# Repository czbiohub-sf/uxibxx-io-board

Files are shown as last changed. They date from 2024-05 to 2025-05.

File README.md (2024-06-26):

# uxibxx-io-board
## Introduction
This repository contains the hardware design data, firmware and a Python driver implementation for the UXIB*xx* "family" of digital I/O board~~s~~. This project is intended to provide minimum-friction tools for interfacing Python code to electrical stuff (turning loads on and off, reading switches, etc) in laboratory automation projects.

Currently the device "family" consists of a single example, UXIB-DN12, designed to control a bank of 12 loads such as solenoid valves.

## Directory contents
- `driver/` contains the `uxibxx` Python package used to control UXIB*xx* devices
- `firmware/` contains the source code for the AVR firmware
- `pcb/` contains the KiCAD EDA project files for the UXIB-DN12 PCB

## Getting started
If starting with an already-made UXIB*xx* device, just install the included `uxibxx` package and review the associated API documentation. No extra system-level driver is required on Windows, MacOS or Linux.

See the `README.md` in each subdirectory for further information.

## Licenses
Software source code is licensed under the BSD 3-Clause License. Hardware design files are licensed under CERN-OHL-W.
See the `LICENSE` file in each subdirectory for a copy of the applicable license terms.

## Support
This project is maintained by Greg Courville of the Bioengineering Platform at Chan Zuckerberg Biohub San Francisco.

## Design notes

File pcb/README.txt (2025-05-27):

This directory has KiCAD 8 source files and other documentation for the UXIB-DN12 valve/relay controller board:

soldriver_sch.pdf            Printable UXIB-DN12 schematic
soldrive_assembly_front.pdf  UXIB-DN12 component placement drawing, front side
soldrive_assembly_back.pdf   UXIB-DN12 component placement drawing, rear side

soldriver.kicad_pro          UXIB-DN12 KiCAD 8 project file
soldriver.kicad_sch          UXIB-DN12 schematic
soldriver.kicad_pcb          UXIB-DN12 PCB layout
footprints.pretty/           Project footprint library
sym/                         Project symbol library

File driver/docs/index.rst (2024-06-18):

``uxibxx`` module
=========================

Driver class
------------
.. autoclass:: uxibxx.UxibxxIoBoard
   :members: __init__, list_connected_devices, open_first_device, from_serial_portname, get_direction, set_direction, get_input, get_output, set_output, board_model, board_id, terminal_nos, input_nos, output_nos
   :member-order: bysource

Enums
-----
.. autoclass:: uxibxx.UxibxxIoBoard.IoDirection
   :members:

Exceptions
----------
.. autoclass:: uxibxx.UxibxxIoBoard.UxibxxIoBoardError
.. autoclass:: uxibxx.UxibxxIoBoard.DeviceNotFound
   :show-inheritance: True
.. autoclass:: uxibxx.UxibxxIoBoard.IdMismatch
   :show-inheritance: True
.. autoclass:: uxibxx.UxibxxIoBoard.InvalidTerminalNo
   :show-inheritance: True
.. autoclass:: uxibxx.UxibxxIoBoard.Unsupported
   :show-inheritance: True
.. autoclass:: uxibxx.UxibxxIoBoard.RemoteError
   :show-inheritance: True
.. autoclass:: uxibxx.UxibxxIoBoard.ResponseTimeout
   :show-inheritance: True
.. autoclass:: uxibxx.UxibxxIoBoard.BadResponse
   :show-inheritance: True

Usage example
-------------
.. literalinclude:: usage_example.py
   :language: python

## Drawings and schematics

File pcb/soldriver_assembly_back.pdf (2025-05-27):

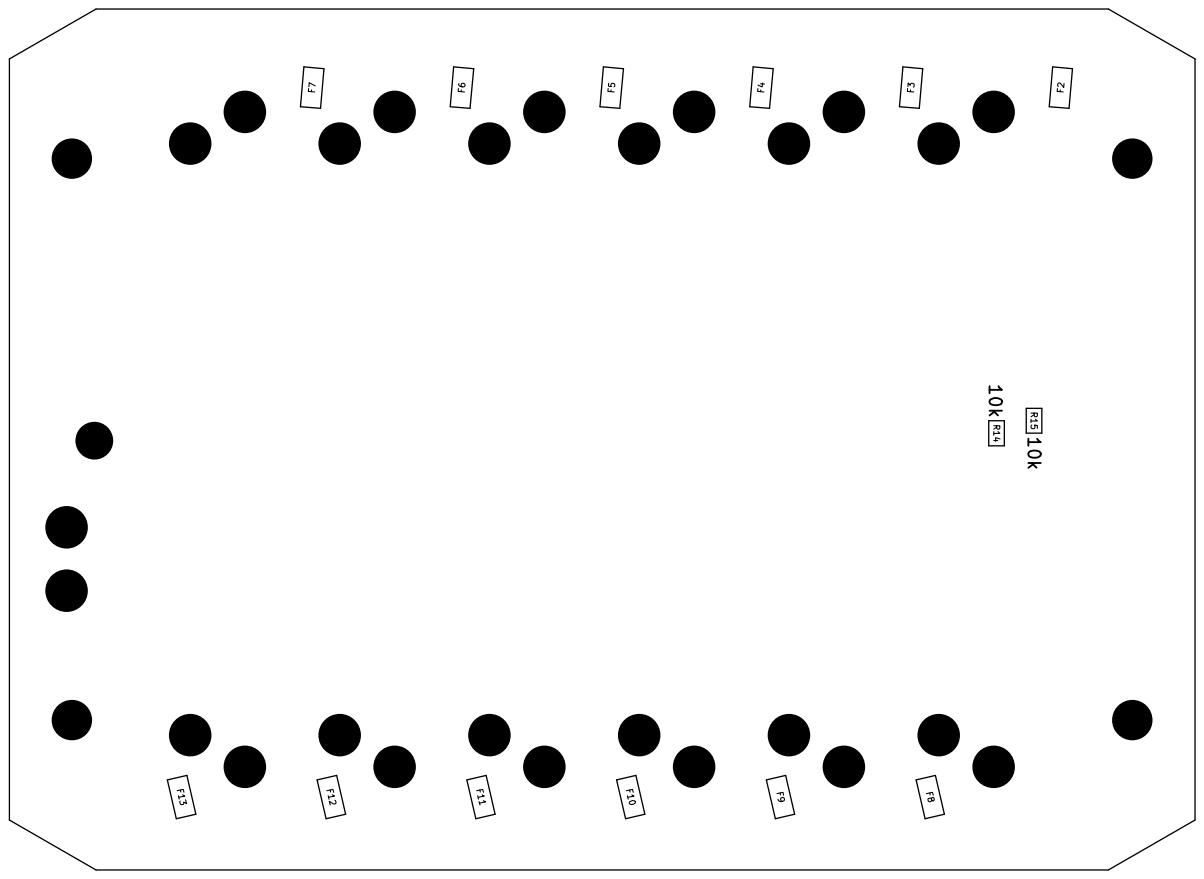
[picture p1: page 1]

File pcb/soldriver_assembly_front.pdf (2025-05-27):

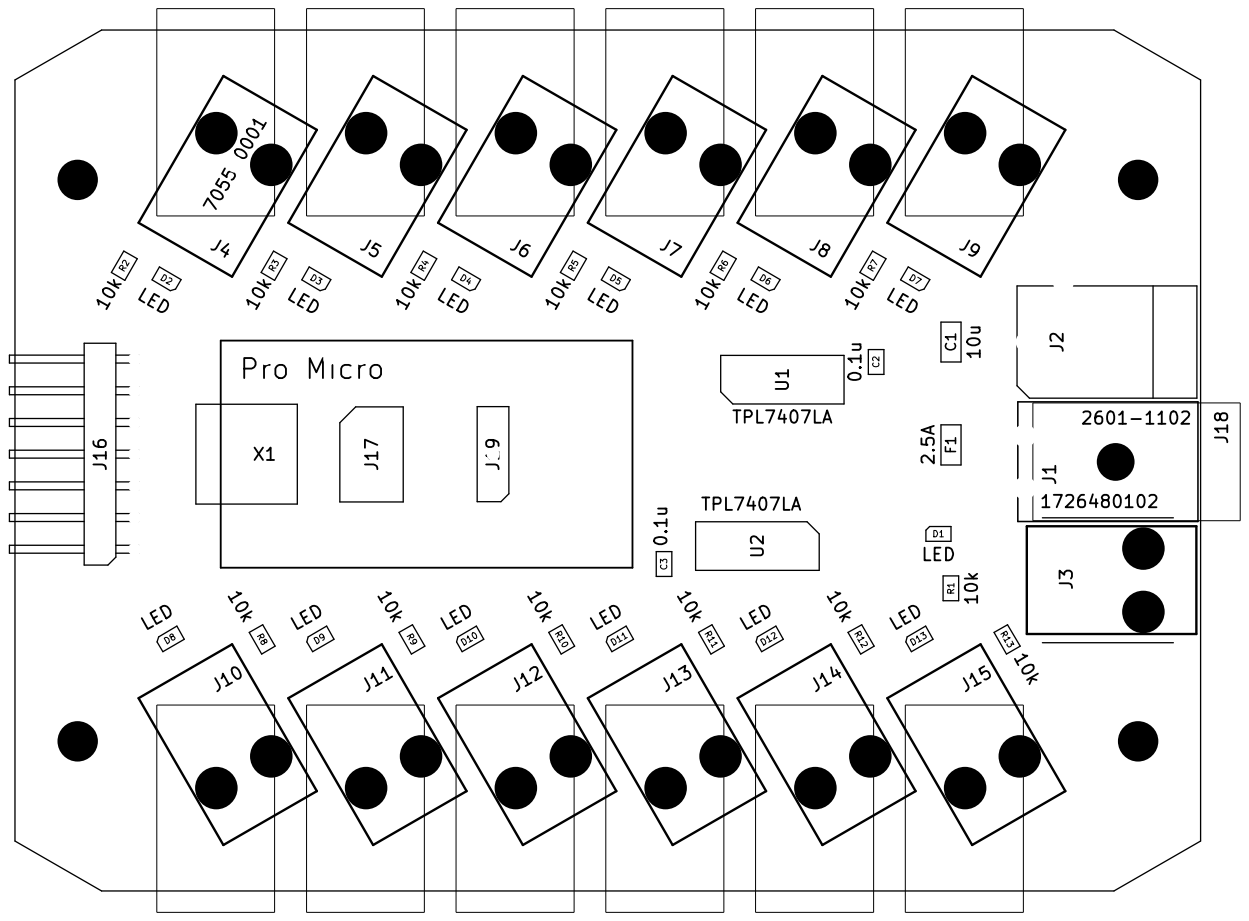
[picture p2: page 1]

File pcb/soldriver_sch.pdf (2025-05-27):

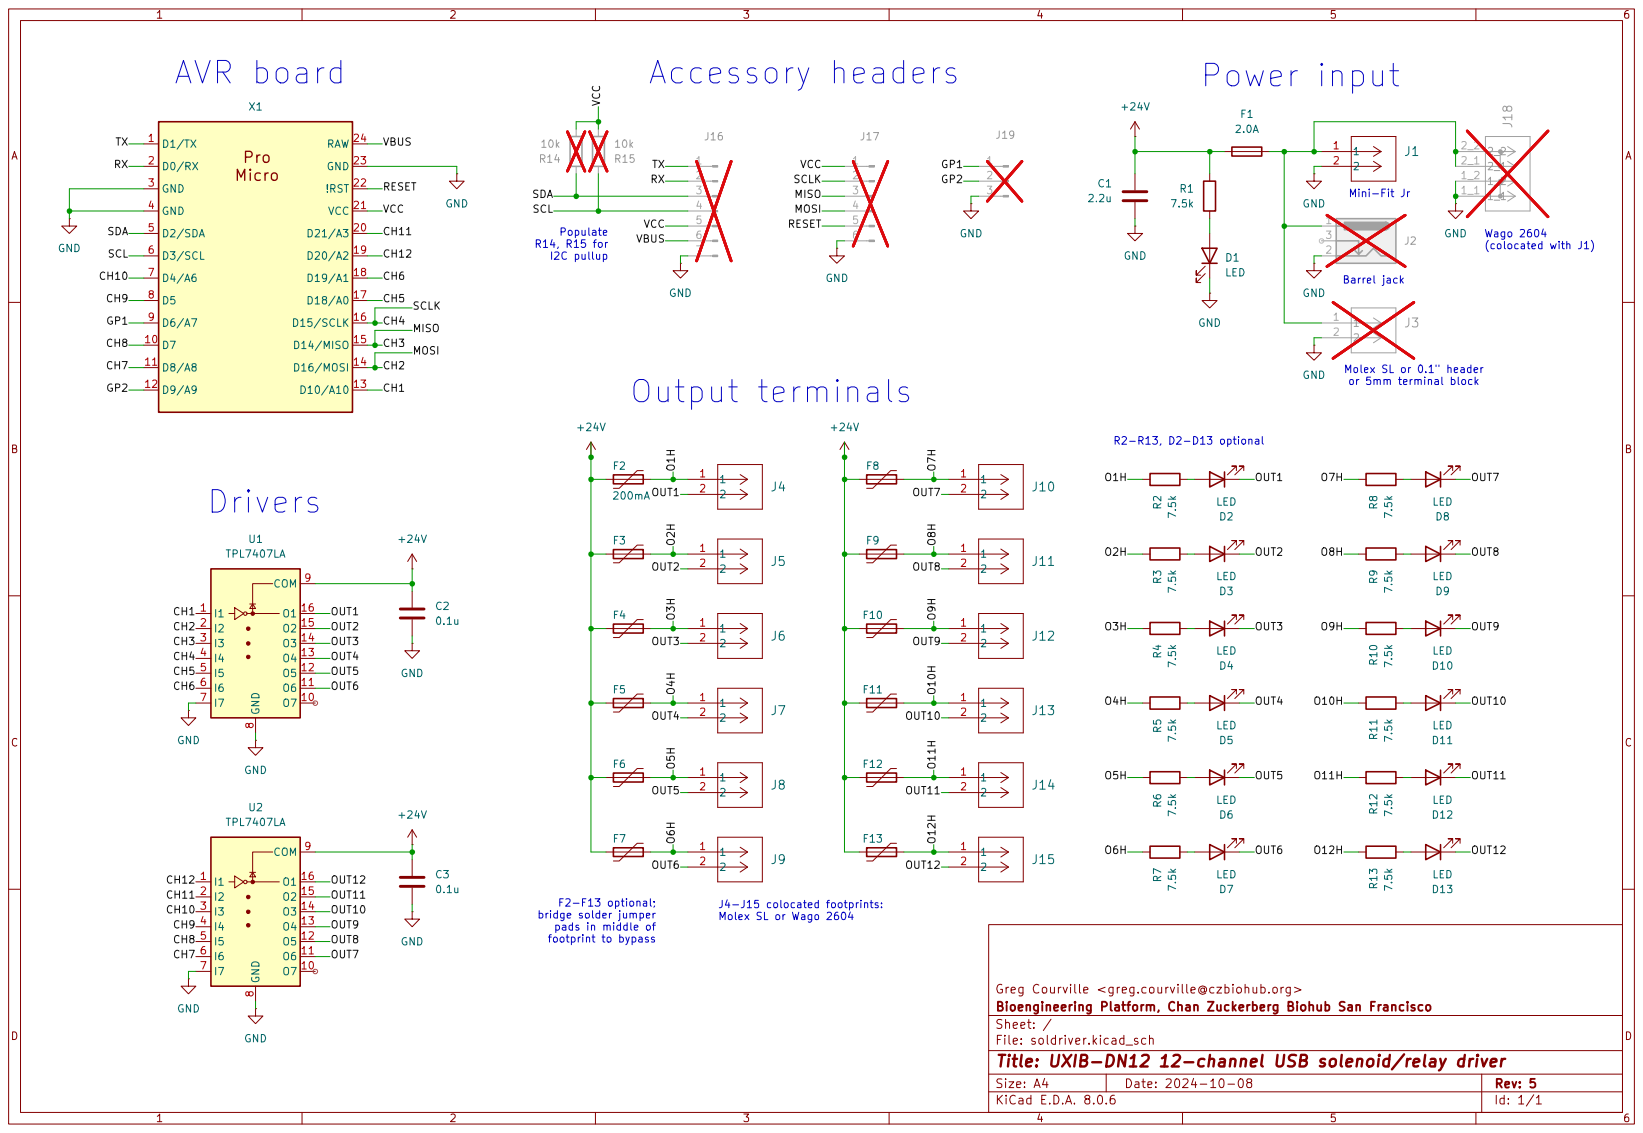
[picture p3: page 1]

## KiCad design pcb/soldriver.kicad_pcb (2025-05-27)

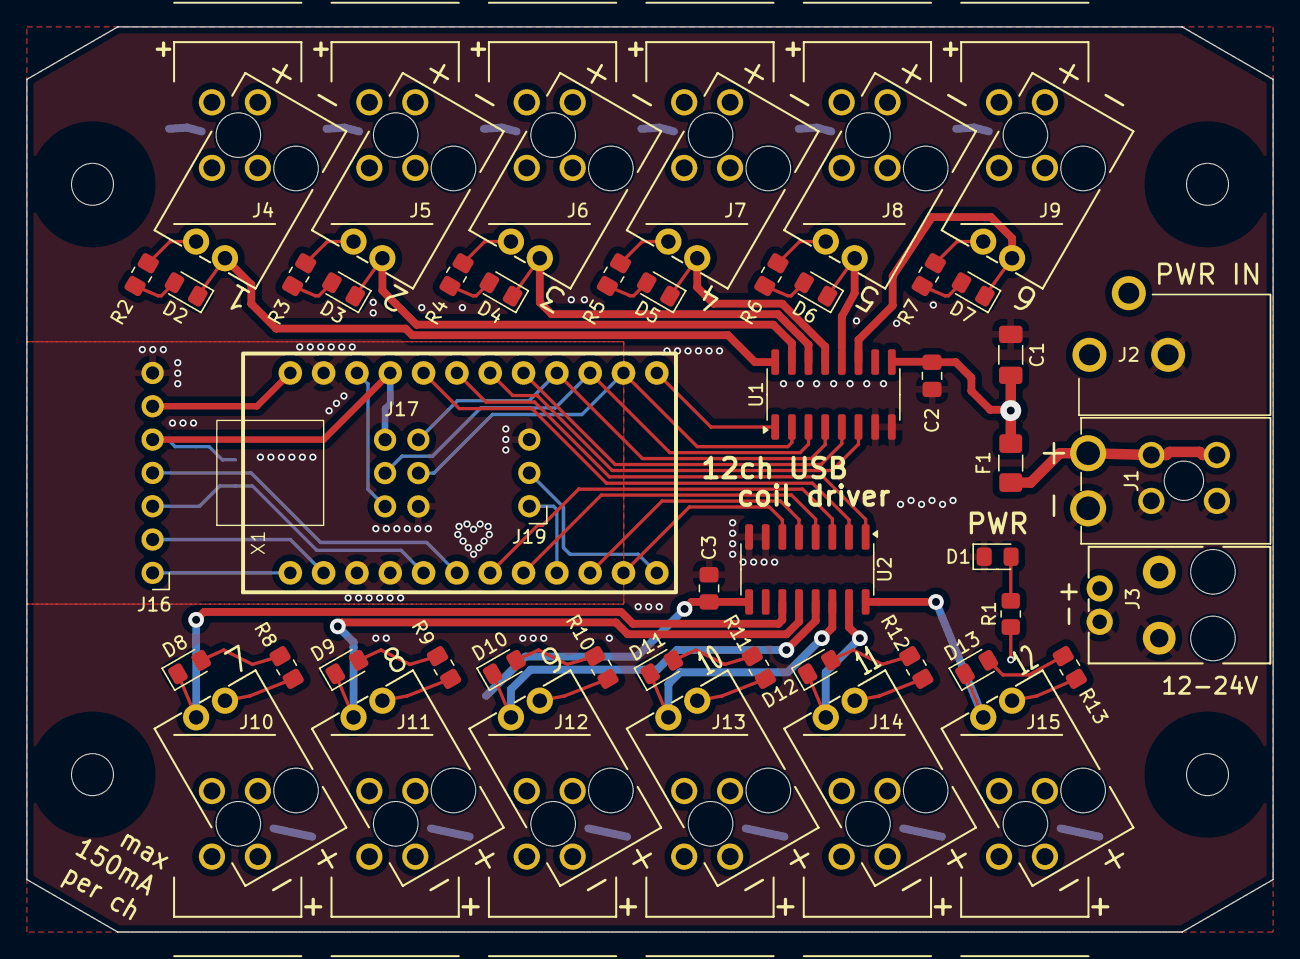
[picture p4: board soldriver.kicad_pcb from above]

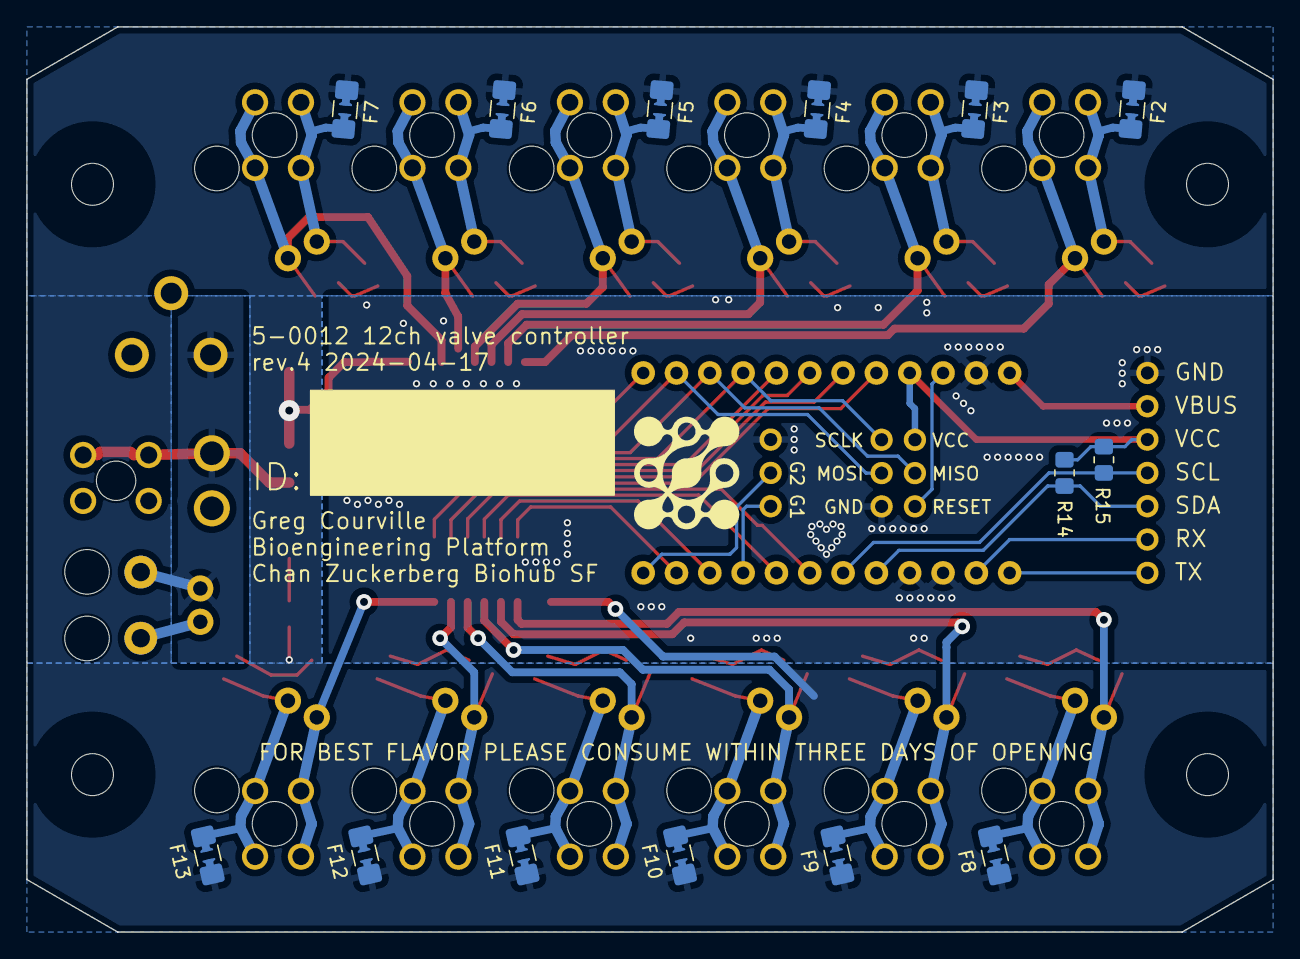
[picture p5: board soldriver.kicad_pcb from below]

Board: 2 copper layers, 95.0 x 69.0 mm, 70 parts (14 on the bottom side), 61 nets.

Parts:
C1: 10u; C_1206_3216Metric_Pad1.33x1.80mm_HandSolder
C2, C3: 0.1u; C_0805_2012Metric_Pad1.18x1.45mm_HandSolder
D1, D2, D3, D4, D5, D6, D7, D8, D9, D10, D11, D12, D13: LED; LED_0805_2012Metric_Pad1.15x1.40mm_HandSolder
F1: 2.5A; Fuse_1206_3216Metric_Pad1.42x1.75mm_HandSolder
F2, F3, F4, F5, F6, F7, F8, F9, F10, F11, F12, F13: Polyfuse; fuse_1206_jumperable
J1: 1726480102; CON_1726480102
J2: Barrel_Jack_Switch; CUI_PJ-102AH_with3dmodel
J3: 1726480102; molex_705510001_or_2pos_5mm_tb
J4, J5, J6, J7, J8, J9: 705510001; molex_705510001_or_wago_2601-1102_lh
J10, J11, J12, J13, J14, J15: 705510001; molex_705510001_or_wago_2601-1102_rh
J16: Conn_01x08_Pin; PinHeader_1x07_P2.54mm_Horizontal
J17: Conn_01x08_Pin; PinHeader_2x03_P2.54mm_Vertical
J18: 2601-1102; CONN_2601-1102_WAG
J19: Conn_01x03_Pin; PinHeader_1x03_P2.54mm_Vertical
MH1, MH2, MH3, MH4: MountingHole_3.2mm_M3
R1, R2, R3, R4, R5, R6, R7, R8, R9, R10, R11, R12, R13, R14, R15: 10k; R_0805_2012Metric_Pad1.20x1.40mm_HandSolder
U1, U2: TPL7407LA; SOIC-16_3.9x9.9mm_P1.27mm
X1: promicro_in_socket

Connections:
+24V: C1.1, C2.1, C3.1, F1.1, F2.1, F3.1, F4.1, F5.1, F6.1, F7.1, F8.1, F9.1, F10.1, F11.1, F12.1, F13.1, R1.1, U1.9 (COM), U2.9 (COM)
/CH1: U1.1 (I1), X1.13 (D10/A10)
/CH2: J17.4, U1.2 (I2), X1.14 (D16/MOSI)
/CH3: J17.3, U1.3 (I3), X1.15 (D14/MISO)
/CH4: J17.2, U1.4 (I4), X1.16 (D15/SCLK)
/CH5: U1.5 (I5), X1.17 (D18/A0)
/CH6: U1.6 (I6), X1.18 (D19/A1)
/CH7: U2.6 (I6), X1.11 (D8/A8)
/CH8: U2.5 (I5), X1.10 (D7)
/CH9: U2.4 (I4), X1.8 (D5)
/CH10: U2.3 (I3), X1.7 (D4/A6)
/CH11: U2.2 (I2), X1.20 (D21/A3)
/CH12: U2.1 (I1), X1.19 (D20/A2)
/GP1: J19.1, X1.9 (D6/A7)
/GP2: J19.2, X1.12 (D9/A9)
/O1H: F2.2, J4.1, R2.1
/O2H: F3.2, J5.1, R3.1
/O3H: F4.2, J6.1, R4.1
/O4H: F5.2, J7.1, R5.1
/O5H: F6.2, J8.1, R6.1
/O6H: F7.2, J9.1, R7.1
/O7H: F8.2, J10.1, R8.1
/O8H: F9.2, J11.1, R9.1
/O9H: F10.2, J12.1, R10.1
/O10H: F11.2, J13.1, R11.1
/O11H: F12.2, J14.1, R12.1
/O12H: F13.2, J15.1, R13.1
/OUT1: D2.1 (K), J4.2, U1.16 (O1)
/OUT2: D3.1 (K), J5.2, U1.15 (O2)
/OUT3: D4.1 (K), J6.2, U1.14 (O3)
/OUT4: D5.1 (K), J7.2, U1.13 (O4)
/OUT5: D6.1 (K), J8.2, U1.12 (O5)
/OUT6: D7.1 (K), J9.2, U1.11 (O6)
/OUT7: D8.1 (K), J10.2, U2.11 (O6)
/OUT8: D9.1 (K), J11.2, U2.12 (O5)
/OUT9: D10.1 (K), J12.2, U2.13 (O4)
/OUT10: D11.1 (K), J13.2, U2.14 (O3)
/OUT11: D12.1 (K), J14.2, U2.15 (O2)
/OUT12: D13.1 (K), J15.2, U2.16 (O1)
/RESET: J17.5, X1.22 (!RST)
/RX: J16.2, X1.2 (D0/RX)
/SCL: J16.4, R15.1, X1.6 (D3/SCL)
/SDA: J16.3, R14.1, X1.5 (D2/SDA)
/TX: J16.1, X1.1 (D1/TX)
/VBUS: J16.6, X1.24 (RAW)
/VCC: J16.5, J17.1, R14.2, R15.2, X1.21 (VCC)
GND: C1.2, C2.2, C3.2, D1.1 (K), J1.2, J2.2, J3.2, J16.7, J17.6, J18.1_1, J18.1_2, J19.3, U1.7 (I7), U1.8 (GND), U2.7 (I7), U2.8 (GND), X1.3 (GND), X1.4 (GND), X1.23 (GND)
unnamed: D1.2 (A), R1.2
unnamed: D2.2 (A), R2.2
unnamed: D3.2 (A), R3.2
unnamed: D4.2 (A), R4.2
unnamed: D5.2 (A), R5.2
unnamed: D6.2 (A), R6.2
unnamed: D7.2 (A), R7.2
unnamed: D8.2 (A), R8.2
unnamed: D9.2 (A), R9.2
unnamed: D10.2 (A), R10.2
unnamed: D11.2 (A), R11.2
unnamed: D12.2 (A), R12.2
unnamed: D13.2 (A), R13.2
unnamed: F1.2, J1.1, J2.1, J3.1, J18.2_1, J18.2_2

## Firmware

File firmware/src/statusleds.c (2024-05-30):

#include <stdint.h>
#include <avr/io.h>


#define LED_HBT_PORT PORTD
#define LED_HBT_DDR DDRD
#define LED_HBT_BM _BV(PD5)
#define LED_USB_PORT PORTB
#define LED_USB_DDR DDRB
#define LED_USB_BM _BV(PB0)

#define HEARTBEAT_HALFPERIOD_MS 500
#define WINK_DURATION_MS 60
#define WINK_RECOVERY_MS 40


volatile uint16_t currentTick;
volatile uint16_t lastHbtChangeTick;
volatile uint16_t winkStartTick;
volatile struct {
	unsigned int winking :1;
	unsigned int winkCooldown :1;
	unsigned int hbt :1;
	} volFlags;
struct {
	unsigned int usbLedSetting :1;
	unsigned int hbtAck :1;
	unsigned int startWink :1;
	} flags;


inline void setHbtLed(int on) {
	if(on) {
		LED_HBT_PORT &= ~LED_HBT_BM;
		}
	else {
		LED_HBT_PORT |= LED_HBT_BM;
		}
	}

inline void toggleHbtLed(void) {
	LED_HBT_PORT ^= LED_HBT_BM;
	}

inline void setUsbLed(int on) {
	if(on) {
		LED_USB_PORT &= ~LED_USB_BM;
		}
	else {
		LED_USB_PORT |= LED_USB_BM;
		}
	}

void statusleds__init(void) {
	setHbtLed(0);
	setUsbLed(0);
	LED_HBT_DDR |= LED_HBT_BM;
	LED_USB_DDR |= LED_USB_BM;
	lastHbtChangeTick = 0;
	volFlags.winking = 0;
	volFlags.winkCooldown = 0;
	volFlags.hbt = 0;
	flags.usbLedSetting = 0;
	flags.hbtAck = 0;
	flags.startWink = 0;
	}

void statusleds__setHbtLed(int on) {
	setHbtLed(on);
	}

void statusleds__setUsbLed(int on) {
	flags.usbLedSetting = !!on;
	setUsbLed(on);
	}

void statusleds__winkUsbLed(void) {
	flags.startWink = 1;
	}

void statusleds__onMsTick(volatile uint16_t *msCounter) {
	currentTick = *msCounter;
	if(flags.hbtAck) {
		volFlags.hbt = 0;
		}
	else if(currentTick - lastHbtChangeTick >= HEARTBEAT_HALFPERIOD_MS) {
		volFlags.hbt = 1;
		lastHbtChangeTick = currentTick;
		}
	if(volFlags.winkCooldown) {
		if(currentTick - winkStartTick >= WINK_DURATION_MS + WINK_RECOVERY_MS) {
			volFlags.winking = 0;
			volFlags.winkCooldown = 0;
			}
		}
	else if(volFlags.winking) {
		if(currentTick - winkStartTick >= WINK_DURATION_MS) {
			setUsbLed(flags.usbLedSetting);
			volFlags.winkCooldown = 1;
			}
		}
	else if(flags.startWink) {
		winkStartTick = currentTick;
		setUsbLed(0);
		volFlags.winking = 1;
		}
	}

void statusleds__task(void) {
	if(flags.hbtAck) {
		if(!volFlags.hbt)
			flags.hbtAck = 0;
		}
	else if(volFlags.hbt) {
		toggleHbtLed();
		flags.hbtAck = 1;
		}
	if(flags.startWink) {
		if(volFlags.winking)
			flags.startWink = 0;
		}
	}

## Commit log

2024-05-30 initial fw with LED blinking and skeleton for CDC ACM comms
2024-05-30 added PCB files
    [soldriver.kicad_pcb, soldriver.kicad_sch]
2024-05-30 change temp io assignments to not touch LEDs
2024-05-30 actual i/o assignments for DN12 board
2024-06-26 add license info for pcb
2024-10-08 switch to 2.2uF tantalum cap
    [soldriver.kicad_sch]
2025-05-27 update DN12 schematic title block and add PDF
    [soldriver.kicad_sch]
2025-05-27 add front and back component placement drawings
    [soldriver.kicad_pcb]
